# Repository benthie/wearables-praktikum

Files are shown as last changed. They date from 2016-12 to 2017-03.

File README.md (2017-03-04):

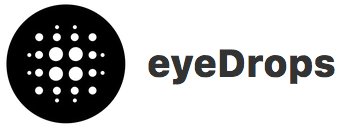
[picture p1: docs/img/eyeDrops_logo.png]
<br>
<i>     a project by Marlene Fiedler, Lorenz Miething and Benjamin Thiemann</i><br>
<br>
In the context of the lab course "Wearable Computing Systems", which started at the end of Oct 2016, we were asked to build our own wearable device. Our idea since then was to build a blink detection system that recognizes the user's lack of blinking when sitting in front of the computer. With a distance sensor that is monitoring the eye and a custom-built software the user of our wearable will be stimulated to blink by blurring the computer screen.

#Documentation

Now - at the end of the project - we proudly present our results. All the single bits and pieces of our project have been documented in order to deliver high reusability for anybody who wants to work on the project after the end of the semester the lab took place. This repository is mainly devided into the two sub parts hardware and software. The hardware itself consists of two different PCBs and the fixation parts to fix the PCBs to different kinds of glasses, as well as 3D printed glasses for users who usually do not wear any. All documenting files should enable you to rebuild the hardware such that you have a working system, which will be accepted by the software parts and then run without difficulty.<br>
<br>
The developed software has been published under the open source MIT License and is running as it is. It consists of two parts, namely an RFduino sketch and a Mac OS X Cocoa application. The sketch for the RFduino contains the blink detection algorithm and is able to communicate with the Cocoa app via Bluetooth Low Energy. For detailed information about the blink detection algorithm please see [here](#eye-blink-detection-algorithm). The Cocoa app's source code has both copious commenting and a [Doxygen documentation](https://benthie.github.io/wearables-praktikum/). The application's graphical user interface will be explained [below](#eyedrops-cocoa-application) and is additionally explained in a short [video](https://youtu.be/3qRnkdi4qJQ).

##Table of contents
- [Requirements](#requirements)
- [How to use](#how-to-use)
- [Hardware](#hardware)
  - [VCNL4020](#vcnl4020)
  - [RFduino](#rfduino)
  - [3D-printed parts](#3d-printed-parts)
- [Eye blink detection algorithm](#eye-blink-detection-algorithm)
- [eyeDrops Cocoa Application](#eyedrops-cocoa-application)
  - [Blur mode](#blur-mode)
  - [Bluetooth connection](#establishing-bluetooth-le-connection)
  - [User profile manager](#user-profile-manager)
  - [Preferences](#preferences)
  - [Calibration](#calibration)
  - [Ready to use](#ready-to-use)
  - [Executable File](#executable-file)
  - [Doxygen documentation](https://benthie.github.io/wearables-praktikum/)
- [Live Demo](#live-demo)
- [Credits](#credits)
- [License](#license)

###Requirements
- Arduino IDE ([Arduino software](https://www.arduino.cc/en/main/software)) 
- RFduino Package ([Link to the Git](https://github.com/RFduino/RFduino/blob/master/README.md))
- Mac OS X (sorry for that crucial restriction!)
- Bluetooth Low Energy (BLE - also called Bluetooth 4.0) capable Mac
- RFduino USB Shield ([RFD22121](http://www.rfduino.com/product/rfd22121-usb-shield-for-rfduino/index.html) or [RFD22124](http://www.rfduino.com/product/rfd22124-pcb-usb-shield-for-rfduino/index.html))
- CorePlot Framework ([Installation Guide](https://github.com/core-plot/core-plot/wiki/Using-Core-Plot-in-an-Application))

###How to use

So how to use our wearable? Simply grab the 3d-printed clips and the fitting slider, mount the electronics together with a battery pack on it, which then altogether forms the so called "<b>wearable</b>" and make sure that your Mac fullfills the above requirements. Plug the RFduino USB shield into your Mac and upload our [RFduino sketch](software/RFduino) to the wearable. After completing this step the last thing to do is to download the [Xcode project](software/cocoa-app), follow the [CorePlot library installation guide](https://github.com/core-plot/core-plot/wiki/Using-Core-Plot-in-an-Application) and start the eyeDrops application and have fun exploring.<br>
<br>
<i>Note:</i> If you want to use the compiled and built application (.app file) please follow the steps described in section [Executable File](#executable-file).

#Hardware

Our Hardware consits mainly of three parts: The sensor that is detecting the blinks, the microcontroller RFduino and our 3D-printed parts, used to hold the sensor and microcontroller in place.

##VCNL4020

The sensor used in our wearable is the VCNL4020 (http://www.vishay.com/docs/83476/vcnl4020.pdf). It is a proximity and ambient light sensor with a built-in infrared emitter and photo diode. The data obtained from the sensor vary, depending on how much light is reflected back to the sensor. Due to its high 16-bit-resolution and the operating range from 1 to 200 mm, it is possible to determine the difference of distance when pointing at an open or a closed eyelid. The data of the VCNL4020 can be transferred via an I²C Interface. Furthermore, interrupts can be sent. 

<p align="center">
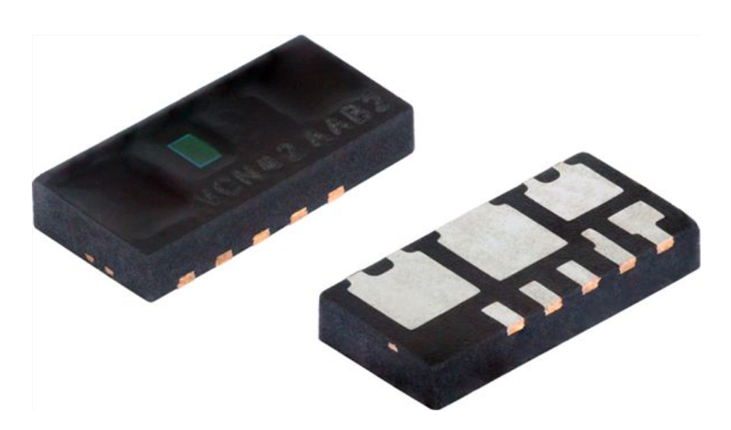
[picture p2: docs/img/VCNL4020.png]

<br>Figure 1: Sensor VCNL4020.
</p>

A custom PCB was designed for the VCNL4020. The goal was to get a board that can be attached to a clip, mounted in the front of spectacles, worn by the user. In order to not disturb the user while working, the PCB should be as small as possible. The first design featured pull-up resistors for the data, clock and interrupt signals, decoupling capacitors and five header pins for power supply, the I²C interface and the interrupt signal. 

<p align="center">
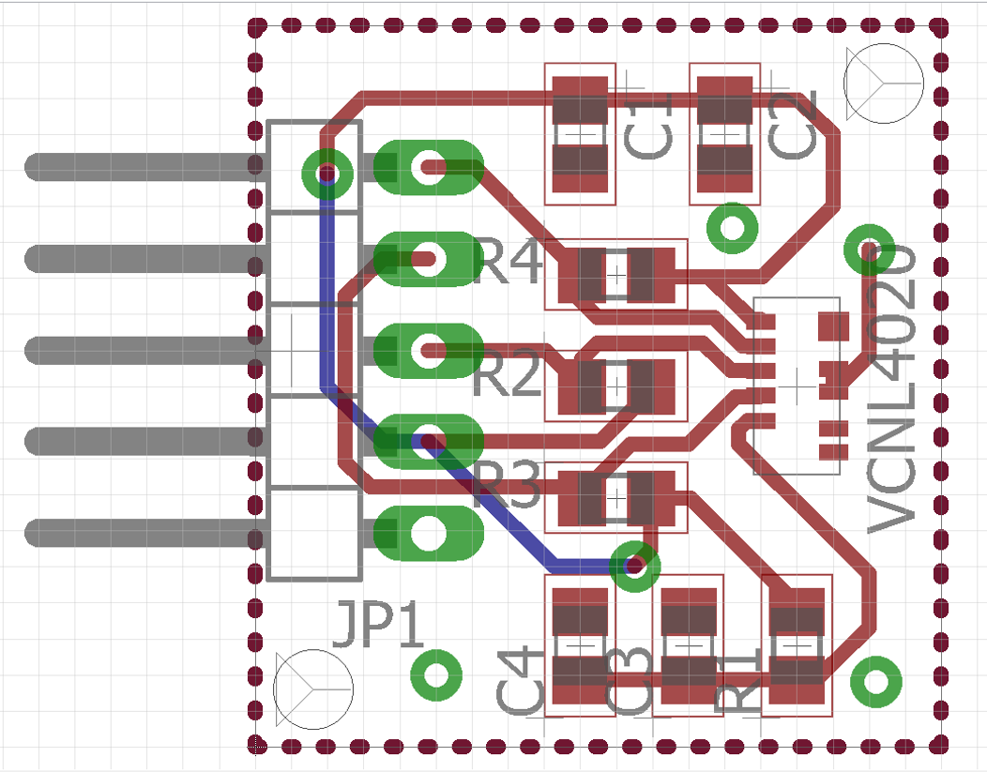
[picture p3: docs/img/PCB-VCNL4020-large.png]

<br>Figure 2: First PCB design for VCNL4020.
</p>

However, the first PCB design had to be revised due to its size, by moving the pull-up resistors to the second PCB and using small pads instead of the header pins. The revised PCB features a size of only 11 mm times 12 mm. The schematics and layouts of both versions  can be found [here](https://github.com/benthie/wearables-praktikum/tree/master/hardware/eagle).

The revised PCB was milled, using a Cirqoid CNC mill (http://cirqoid.com/). Both the milled PCB without components and the populated PCB can be seen here:

<p align="center">
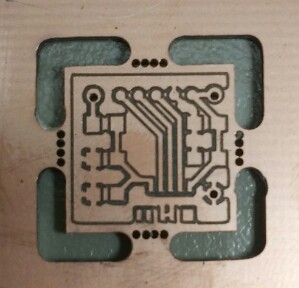
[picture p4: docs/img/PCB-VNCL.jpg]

<br>Figure 3: milled PCB for VCNL4020.
</p>

<p align="center">
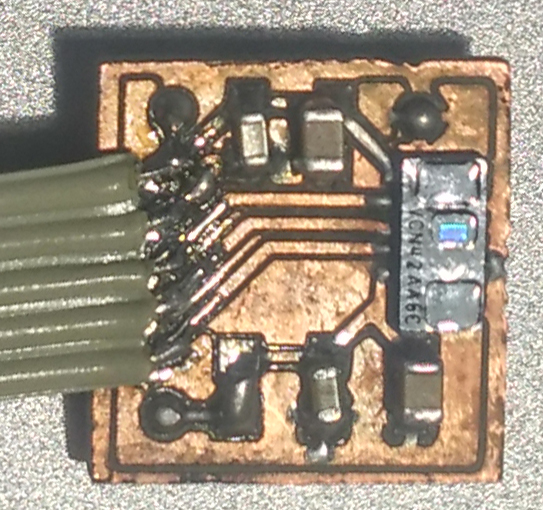
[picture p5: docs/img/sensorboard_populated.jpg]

<br>Figure 4: populated PCB for VCNL4020.
</p>

A ribbon cable was attached to the pads, so that the PCB for the VCNL can be connected to the RFduino PCB, which will be described in the following chapter.

##RFduino

The microcontroller used in our project is an RFduino (http://www.rfduino.com/) which features a bluetooth low energy (BLE) compatible radio transceiver. It can be programmed using the Arduino IDE.

<p align="center">
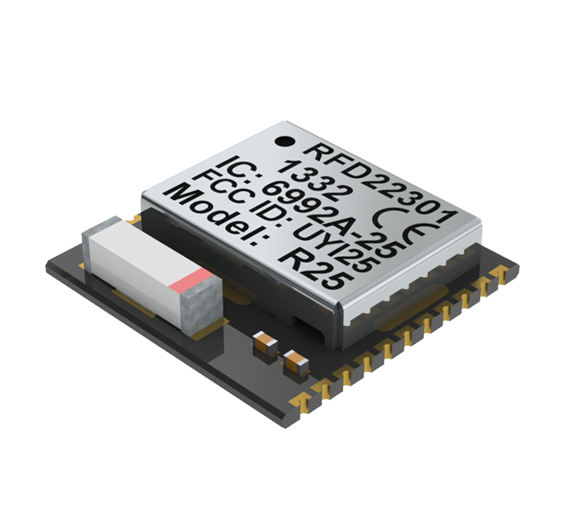
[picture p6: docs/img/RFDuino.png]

<br>Figure 5: RFduino
</p>

A custom PCB was made for the RFduino, featuring a 3.3 V voltage regulator, decoupling capacitors, a reset button, the mentioned pull-up resistors for the VCNL4020, header pins to connect to the ribbon cable leading to the VCNL4020 PCB, header pins for programming the RFduino and a screw terminal for the input voltage. The populated PCB can be seen here:

<p align="center">
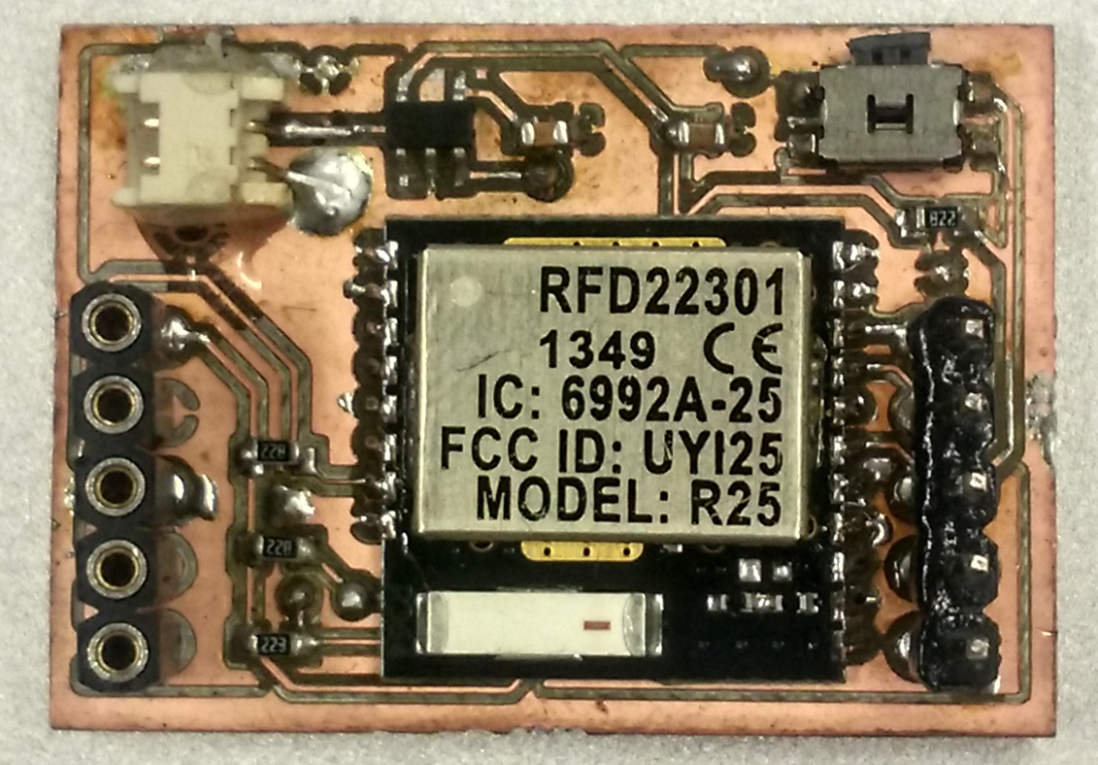
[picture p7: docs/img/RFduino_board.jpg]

<br>Figure 6: PCB for RFduino 
</p>

The schematic and layout of the PCB can be found [here](https://github.com/benthie/wearables-praktikum/tree/master/hardware/eagle).

#Eye blink detection algorithm

The blink detection algorithm can be divided in a filtering and a processing stage. The logarithmically scaled incoming raw data of the sensor are converted into distances of arbitrary unit. Any offset is removed by computing the differences between the samples and an equally weighted moving average filter with a window size of 16 (experimentally determined) is applied to the derivative of the data. With that, the filtering stage is completed and the actual detection algorithm begins, which is applied to the last 200 samples.<br>
Instead of going through all samples within that window for every new sample, the characteristic values are kept in real time as the samples come in.<br>
In order to understand the algorithm more easily let’s first have a look at the pattern that has to be detected. Since the different eye blinks vary in duration and peak height as shown in figure 7, the algorithm has to accomodate for this dynamic behaviour. 
<p align="center">
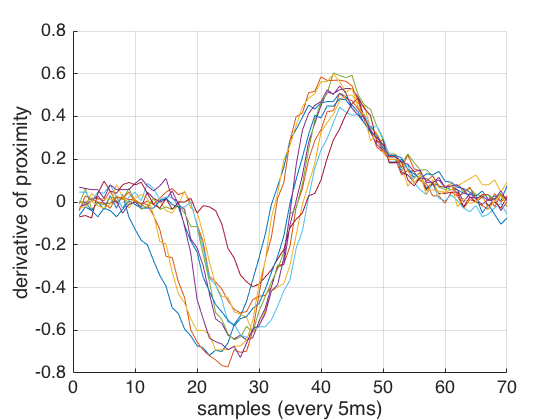
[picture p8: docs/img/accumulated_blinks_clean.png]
Accumulated eye blinks

<br>Figure 7: Accumulated eye blinks with varying durations from single person
</p>
Therefore, a simple pattern correlation would not perform very well. Instead, the algorithm looks for a certain dynamic pattern in the preprocessed data. It performs edge detection and zero crossing detection by comparing the current value with the previous one. The values are split into four areas: above positive threshold, between positive threshold and zero, between zero and negative threshold and below negative threshold. With this in mind six different crossings can be detected creating the following algorithm to detect the actual eye blink as shown in figure 8.
<p align="center">
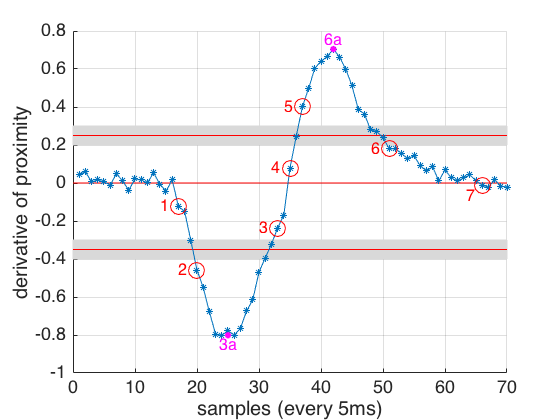
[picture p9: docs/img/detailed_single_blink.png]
Step by step eye blink

<br>Figure 8: Step by step blink detection
</p>
1. Zero has to be crossed from a positive to a negative value. This means that the measured distance is decreasing and the eye lid is closing. Zero was just cross for point 1.
2. The negative threshold is crossed downwards. This means that the measured distance decreases less significantly and the eye lid stops closing.
3. The negative threshold is crossed upwards. At this point the minimum value and its index between the two negative threshold crossings is determined from the sample buffer. If the sample number between the initial zero crossing and the determined minimum value is within a certain range and the minimim value is above a certain value. With that the first neces- sary condition is met and the blink level indicating the progress of the current eye blink to be detected is increased by one.
4. Zero is crossed upwards. This does not affect the algorithm and can happen multiple times with alter- nating downward zero crossings at this stage. The number of zero crossings is recorded for further anal- ysis at a later stage of the algorithm and refers to the duration the eye is closed during an eye blink.
5. The positive threshold is crossed upwards. This means that the eye lid is beginning to open again.
6. The positive threshold is crossed downwards. At this point the maximum value and its index between the two positive threshold crossings is determined. If the sample number between the last minimum value and the maximum value is within a certain range, the number of zero crossings does not exceed a certain limit, the maximum value itself does not exceed a certain value either, and the blink level has a value of 1 indicating a previes eye closing event, the blink level is increased again by one. This means the eye is stopping to open and therefore almost open again. It is now assumed, that an actual eye blink was detected for real time application.<br>If any of the above conditions is not met, the blink level is reset to zero.
7. Zero is crossed downwards. If the overall duration of the eye blink is within a certain range the blink detection is complete, the blink level is reset to zero and an eye blink is reported. This means that the eye is fully open again or at least the eye lid movement cannot be detected by the sensor anymore for the remaining eye opening procedure.

The actual threshold crossing detection is extended with a hysteresis procedure. In order to cross a threshold upwards the threshold plus a hysteresis value has to be crossed.
In order to cross it downwards, the threshold minus a hysteresis value has to be crossed. This ensures, that a small fluctuation in the data caused by noise does not mess up the steps of the algorithm. The hysteresis is shown as a gray area in figure 8.<br>
Testing this algorithm on multiple persons showed that it does not necessarily work out of the box for everybody but certain paramaters such as the thresholds, hysteresis and sample distances between the steps have to be adjusted. As shown in figure 7 the durations and peak values for only a single person differs from eye blink to eye blink. Looking at the data for different persons this varies even more.

##3D-printed parts

The 3D-printed parts include a clip and slider for the VCNL4020 PCB, a clip for the RFduino and spectacles for users who do not usually wear them. These parts were designed using the 3D CAD software Solidworks (http://www.solidworks.de/) and printed using the 3D-printer Makerbot Replicator 2X (https://store.makerbot.com/printers/replicator2x/). The used filament consists of ABS.

<p align="center">

<br>Figure 9: 3D-Printer Makerbot Replicator 2X
</p>

Since our product shall be usable with the users own spectacles, both clips were designed in three different sizes, so that they can be attached to temple arms of different widths. The clip for the VCNL4020 was made as small as possible and printed with transparent filament, in order to reduce the impact in the visual field of the user.

<p align="center">
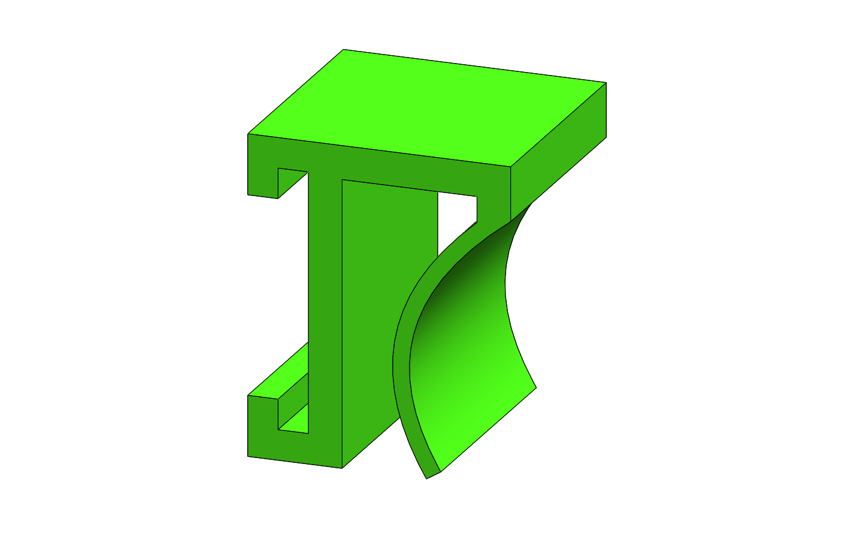
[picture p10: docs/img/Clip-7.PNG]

<br>Figure 10: Clip for VCNL4020 PCB
</p>

Due to different anatomies of different users, like smaller or bigger eyes, eyeballs located further in- or outside the head, etc., it should be possible to adjust the position of the VCNL4020 PCB. Therefore, the PCB is not directly attached to the clip, but instead attached to a slider, which is itself slided into the clip.

<p align="center">
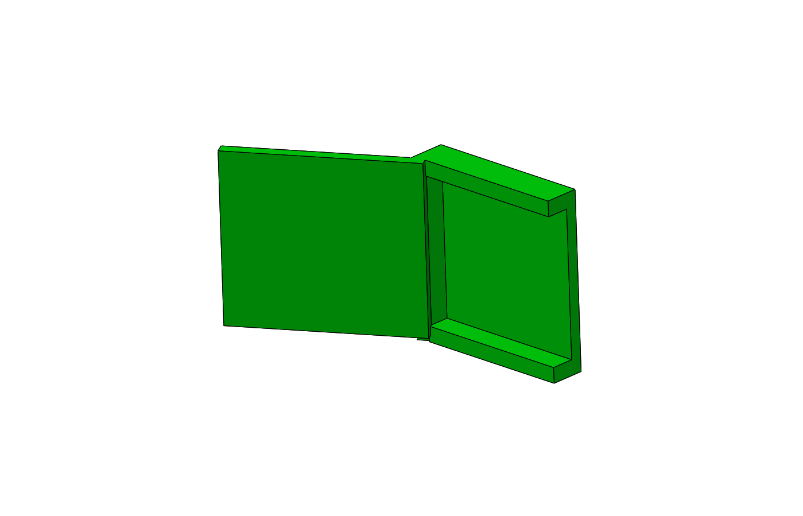
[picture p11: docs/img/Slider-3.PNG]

<br>Figure 11: Slider for VCNL4020 PCB
</p>

The slider was designed with different inclinations, so that the angle between the temple arms and the PCB can be adjusted. There are also sliders that lower the position of the PCB with respect to the height of the temple arms. These exchangable sliders allow adjustment to different anatomies.

<p align="center">
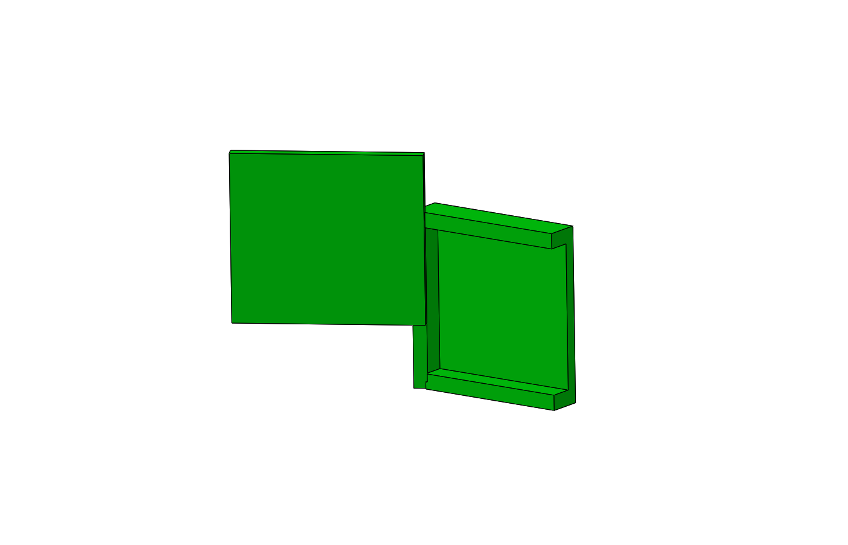
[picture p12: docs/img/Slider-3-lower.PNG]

<br>Figure 12: lower Slider for VCNL4020 PCB
</p>

In order to make adjustments easier, we designed further clips containing magnets. With these, it was possible to attach magnet-containing 3D-printed adapter that were stuck to the PCB. These adapters were also printed with different inclinations, so that, depending on the users anatomy, the sensor would always be well adjusted. However, very thin magnets were not strong enough to hold the adapter in place and thicker magnets were too thick, so that the PCB was encountered disturbing for the user.
Another approach was a 3D-printed ball joint, which could not be used neither, due to the low printing quality for very small round objects. <br>
<br>

In order to attach the RFduino PCB to the users spectacles, there is another clip. This clip is used without a slider. Instead the PCB is directly attached to the clip, held by two tappets. There is a cavity in the clip, so that the reset button of the PCB can be pressed easily.

<p align="center">
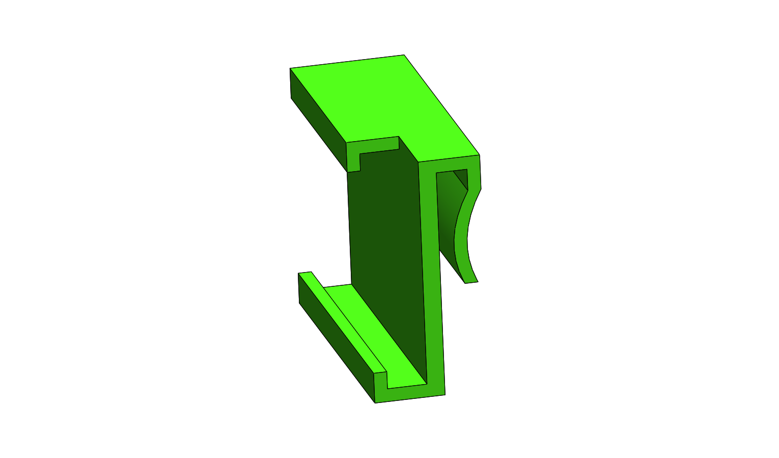
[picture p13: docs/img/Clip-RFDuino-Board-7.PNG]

<br>Figure 13: Clip for RFduino PCB
</p>

The 3D-printed spectacles with the attached clips can be seen in the following graphic:

<p align="center">
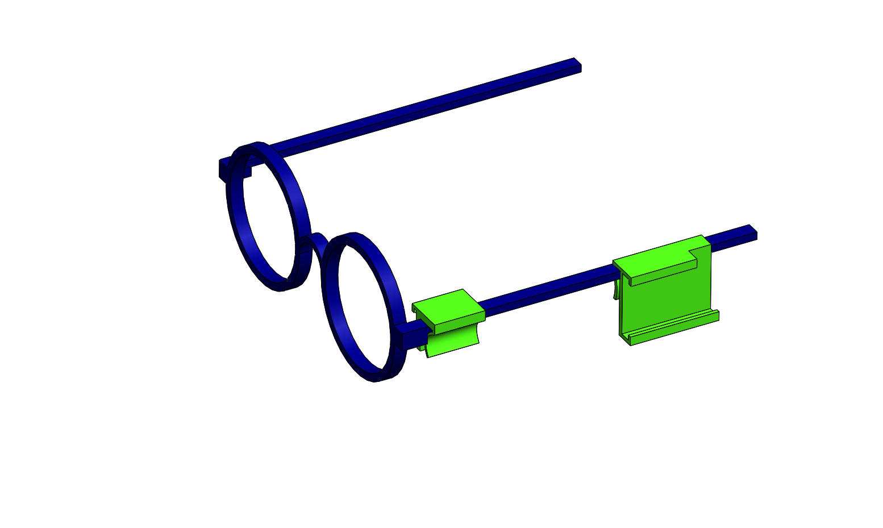
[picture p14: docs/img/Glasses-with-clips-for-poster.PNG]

<br>Figure 14: Spectacles with clips 
</p>

The SLDPRT-files as well as the 3D-printing-files for the described parts can be found [here](https://github.com/benthie/wearables-praktikum/tree/master/hardware/3dprinting).

#eyeDrops Cocoa application

The eyeDrops application is designed to offer a highly comfortable interface between the user and the wearable. The main task of the entire system is to detect a lack of blinking and then react correspondingly. Our implemented reaction to such a lack of blinking is a progressive blurring of the screen in order to enforce an eye blink. A blurred screen can be cleared by a simple blink, which was apparently long overdue. And since the app only needs to control the screen, it was designed as a pure menubar application, that is having no active window but just an icon in the menu bar.<br>
<br>
We chose Mac OS X as the target operating system after a long period of attemps (with a lot of effort) to deliver a platform independent software for our wearable. In the end it was a sum of facts that influenced our decision. The main problem, to begin with, was to build a software that is able to blur the complete screen. Here, Java was the first programming language we tried, but we could not achieve a working version. To do so, one would have to enter a very low level graphics programming since Java cannot make use of a window compositing manager. With Cocoa and Objective-C on the other hand, we could deliver a working blurring of the screen by simply using Quartz Compositor of OS X. In the following process we tried to stick to Java for the main program, but then there was no working BLE stack for Java around that would work on all desired platforms (Windows, Mac, Linux) and thus there was no need to stick to Java anymore. Since two third of the developers were using a Mac and we already had a working software for blurring the screen, it stood to reason that we write the complete software just for Mac. And that is what we did after all.<br>
<br>
To get the eyeDrops application running, download the source code from the [software folder](/software/cocoa-app) and launch `eyeDrops.xcodeproj` with Xcode. Make sure that you properly include the CorePlot framework as described [here](https://github.com/core-plot/core-plot/wiki/Using-Core-Plot-in-an-Application). The project is now ready to be built. The following documentation explains how to use the application you should be able to see now.

##Blur mode

<p align="center">
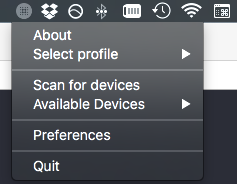
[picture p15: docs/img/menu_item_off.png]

<br>Figure 15: Application in off state.
</p>

As you can see in figure 15, there is no active window but only a menubar icon which pops down a usual menu when you click on it. In the above image the icon is gray and not white, telling the user that blur mode is turned off.

<p align="center">
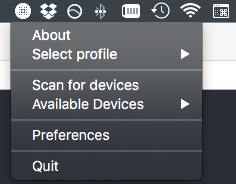
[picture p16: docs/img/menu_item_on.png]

<br>Figure 16: Application in on state.
</p>

In figure 16, however, the icon is white and thus signalizing that blur mode is activated. To switch bewteen those two states simply <b>ctrl-click</b> on the menubar item. If blur mode is actived and in case that a device is connected, the screen would be blurred if the user did not blink in adjustable time interval. See the [settings](#preferences) section for more information about the allowed time interval without an eye blink.

##Establishing Bluetooth (LE) Connection<a name="establishing-bluetooth-le-connection" />

In order to establish a bluetooth connection with the wearable, which is the next necessary and logical step when setting up the system, the first thing to do is scanning for bluetooth nearby. This can be either done via the menuitem <i>Scan for devices</i> or automatically by the app. The latter way needs a setting in the <i>General</i> tab in the [Preferences Window](#preferences).<br>
<br>
After a successful scan all the available devices are listed in the submenu <i>Available Devices</i>. Connecting to the device can again be done either via selecting the corresponding menuitem or automatically by the app. The second way needs a setting in the <i>General</i> tab in the [Preferences Window](#preferences).<br>

<p align="center">
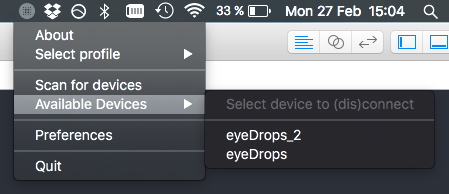
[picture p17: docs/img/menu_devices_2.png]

<br>Figure 17: List of available devices.
</p>

A connected device is represented with a check mark next to its name. Another click on that same menuitem would then cancel the connection with the device. Selecting another device which is currently not the connected one would simply switch the connection to that device.<br>
<br>
In case that a connection was successfully established, the wearable now needs a user profile to work with. This user profile contains the paramerters used by the blink detection algorithm. Without a valid user the wearable will be idle.

##User profiles / profile manager<a name="user-profile-manager" />

In order to obtain a valid user profile either load an XML file containing one or more valid profiles or use the systems [calibration](#calibration) procedure to create a new profile.

<p align="center">
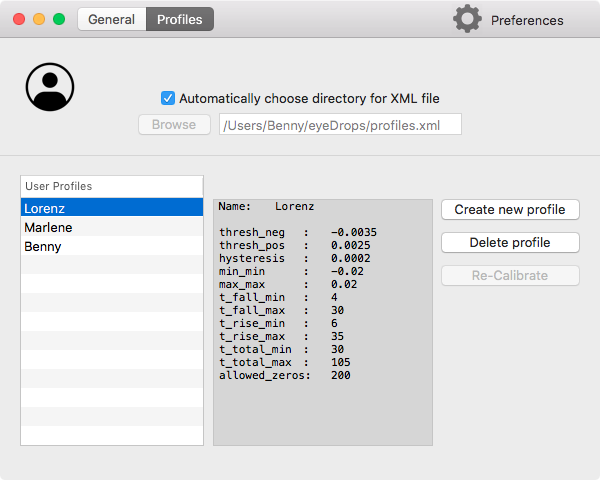
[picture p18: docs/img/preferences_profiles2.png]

<br>Figure 18: Preferences - User profile manager.
</p>

The default directory the app is working in is `/Users/<CurrentUser>/eyeDrops` = `~/eyeDrops`, where `<CurrentUser>` is the name of the currently logged in user. This directory is created during the app's launching process and will of course not be overwritten if it already exists. You can put your XML file in this directory and restart the app, which will lead to an automatic reading of the profiles contained in XML file, or you click <i>Browse</i> in the <i>Profiles</i> tab in the Preferences Window (see figure 18) and manually select your XML file there. After setting the new path, the profiles will be automatically read from the file and displayed in the TableView in the profile manager. Selecting a profile from that table will display the user profile's content in the TextView next to the table. It is also possible to delete a profile by clicking <i>Delete profile</i> or to create a new profile by clicking <i>Create new profile</i>, which will then open up the [calibration window](#calibration).

##Preferences

The system wide settings can be changed in the <i>General</i> tab in the Preferences Window (see figure 19). When starting the eyeDrops app for the first time, this settings will be initialized with values we used during the development phase. When properly closing the app, all made changes will be stored in `settings.txt` in the default directory and reloaded at the next launching process. That way your settings do not get lost.

<p align="center">
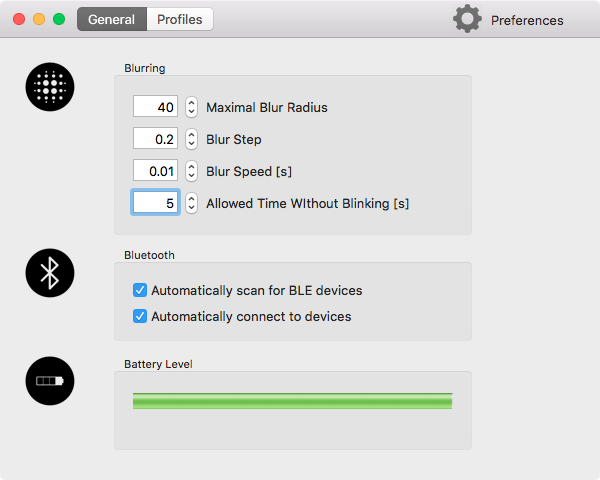
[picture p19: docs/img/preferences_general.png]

<br>Figure 19: Preferences - General settings.
</p>

###Blurring settings
- <b>Maximal Blur Radius:</b> determines how strong your screen gets finally blurred.
- <b>Blur Step:</b> determines the step increase while blurring (the smaller the value, the smoother the blurring).
- <b>Blur Speed:</b> determines the time delay between two steps (the smaller the value, the longer the blurring up to the maximal radius takes).
- <b>Allowed Time Without Blinking:</b> the time interval in which at least one blink has to occur.

###Bluetooth settings
- <b>Automatically scan:</b> determines whether the app automatically scans for devices.
- <b>Automatically connect:</b> determines whether the app automatically connects to the last known device.

###Battery Level
- This LevelIndicator shows the battery level of the wearable. The indication here is not really proportional to the battery voltage but to the voltage after the voltage regulator in the PCB. <!--For more information about this see the [report TODO](/docs/report.pdf).-->

##Calibration

As explained above, calibration is essential for having a properly working blink detection algorithm. Since every eye is unique, differing shapes, sizes and positions in the skull are what the sensor is facing. And due to those inequalities the measured distances to the eye vary from one user to the other. The implemented calibration procedure let's the user define his or her individual calibration parameters, which are then uploaded to the wearable as well as stored in a profile on the computer. More information about the calibration and the different parameters used to detect a blink is elaborately described [above](#eye-blink-detection-algorithm).

<p align="center">
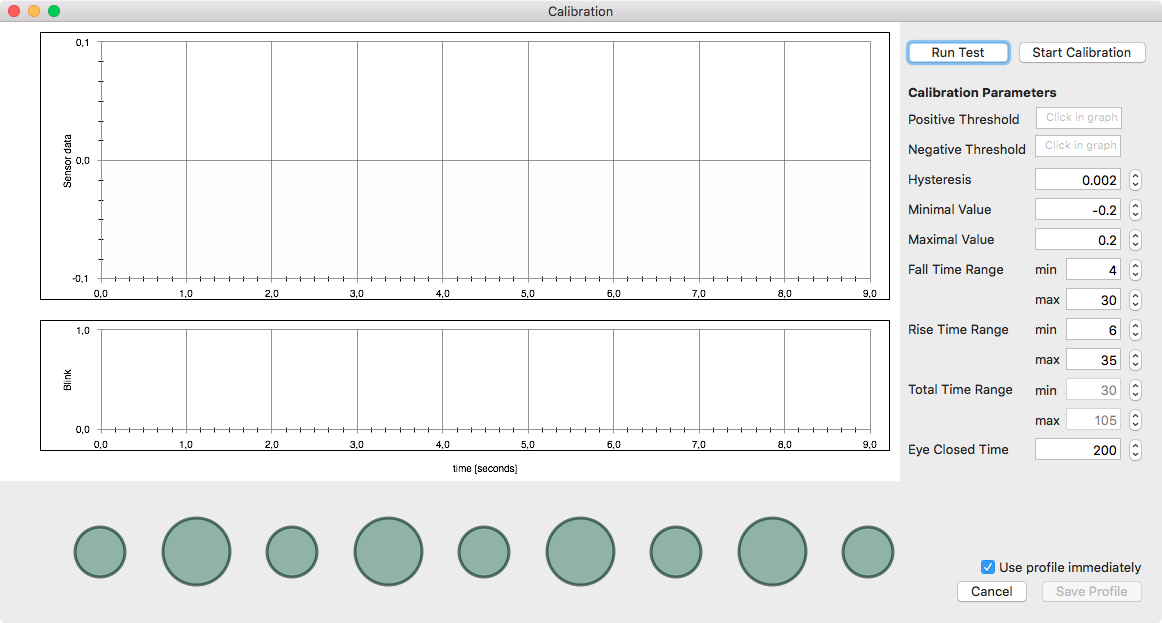
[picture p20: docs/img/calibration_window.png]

<br>Figure 20: Calibration window - On start-up.
</p>

Figure 20 shows the calibration window directly after start-up. Both eyeDrops app and wearable are now in calibration mode  where the RFduino can be triggered to continuously send data packages containing sensor raw data and information about whether a blink was detected or not until a stop message arrives.

<p align="center">

<br>Figure 21: Calibration animation (two successive steps).
</p>

A custom-built animation (see figure 21) is used to guide the user through the data acquisition phase of the calibration. This phase takes nine seconds and should contain four blinks (represented by the larger circles). It can be run testwise without receiving any data, just to get to know the procedure by clicking the button <i>Run Test</i>.<br>
<br>
The completion of the data acquisition will be announced by an pop-up alert with instructions for the next steps. Afterwards the data will be plotted in the two designated graphs.

<p align="center">
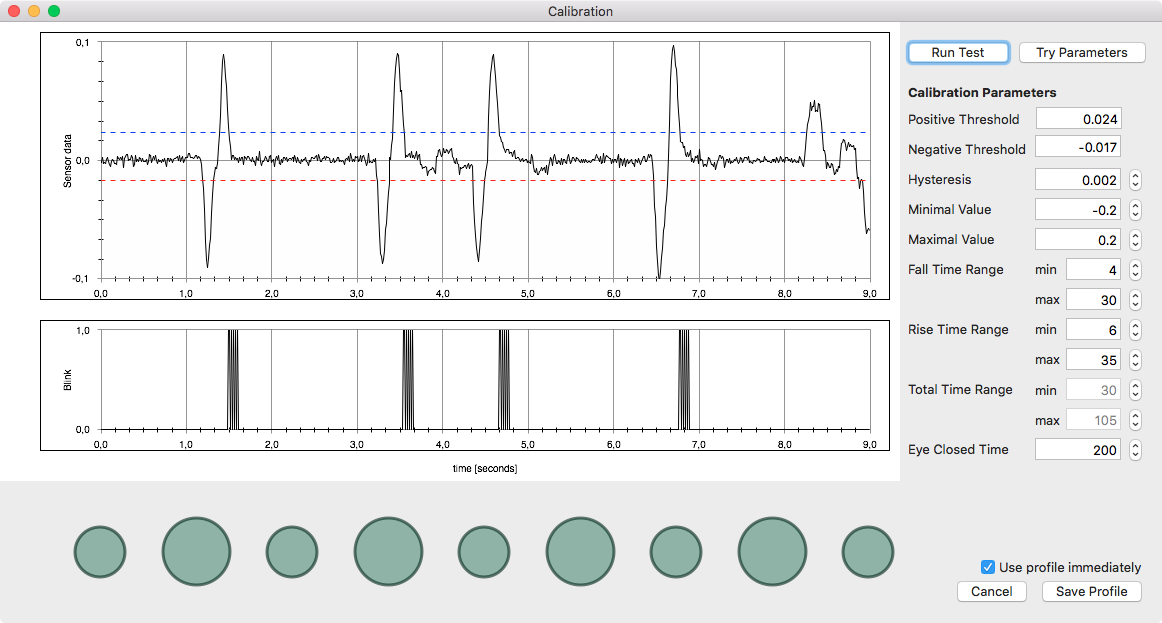
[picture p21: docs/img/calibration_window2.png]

<br>Figure 22: Calibration window - After receiving and plotting the sensor and blink data.
</p>

A completed data acquisition phase can be seen in figure 22. The preset values on the right side of the calibration window turned out to make sense for most of test users and can be adopted for new profiles without being worried about bad performance. The only two values that are mandatory to be set by the user are the threshold values. These can be obtained by simply clicking on the sensor data graph (top). A red and a blue line will appear for negative resprectively positive threshold. Place the lines such that any noise lies between the threshold values. A good guiding value is to set the thresholds to half of it's max value. After setting the threshold values the user can either do another calibration with the newly gained values and check if the algorithm now detects (more) blinks or directly save the profile with the option to directly use the new profile.<br>

###Ready to use

Now that a valid profile has been created and uploaded to the wearable, the system is ready to use. Enable the [blur mode](#blur-mode) and enjoy the experience with the system.

###Using the Cocoa executable (.app file)<a name="executable-file" />

If you do not want to always launch the application out of Xcode, you can use an executable .app file. After running the app out of Xcode, an .app file has been automatically created there. In your project navigator in Xcode you can find it in the `Products` folder. Right-click on `eyeDrops.app` and select `Show in Finder`. The opened folder contains the app as well as two frameworks. Those frameworks must be copied into `/System/Library/Frameworks` to make the `eyeDrops.app` launchable.

##Live Demo

[Link to youtube video](https://www.youtube.com/embed/3qRnkdi4qJQ)

##Credits

<b>The Noun Project - Source for the used items:</b>
- <i>Rohit M S:</i> Creator of the main icon
- <i>Nicolas Morand:</i> Creator of the profiles icon
- <i>Guilhem:</i> Creator of the battery icon
- <i>Viktor Vorobyev:</i> Creator of the bluetooth icon

##License

This project has been published under the MIT License.

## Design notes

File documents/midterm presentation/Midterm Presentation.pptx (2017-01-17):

## Wearable Computing Systems eyeDrops

Lab Course 2016 / 2017
Marlene Fiedler
Lorenz Miething
Benjamin Thiemann

Albert-Ludwigs-Universität Freiburg

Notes: Begrüßung

Name

Thema

## Contents

- Eye blink detection – proof of concept
- Components
- Clip design
- Printed circuit board
- Blurry screen
- Project plan

eyeDrops

## Eye blink detection – Sensors

- Ambient light sensor
  - APDS 9600 RGB ambient light and gesture sensor
    - First success but slow and not robust (active)

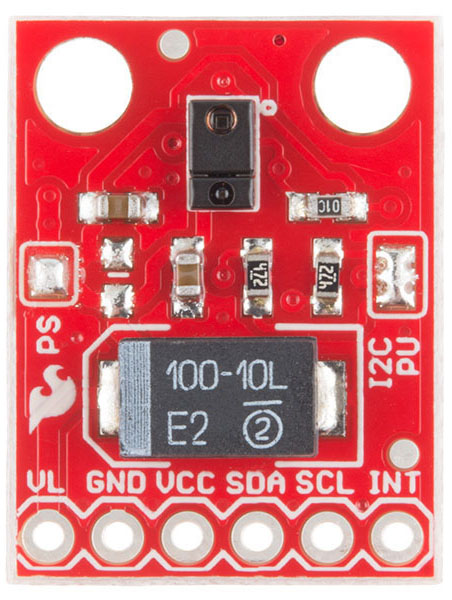
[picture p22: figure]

https://cdn.sparkfun.com//assets/parts/9/6/0/3/12787-02.jpg

## Eye blink detection – Sensors

- Ambient light sensor
  - APDS 9600 RGB ambient light and gesture sensor
  - Self built alternative using photodiode and analogue signal
    - Very fast but not robust (passive)

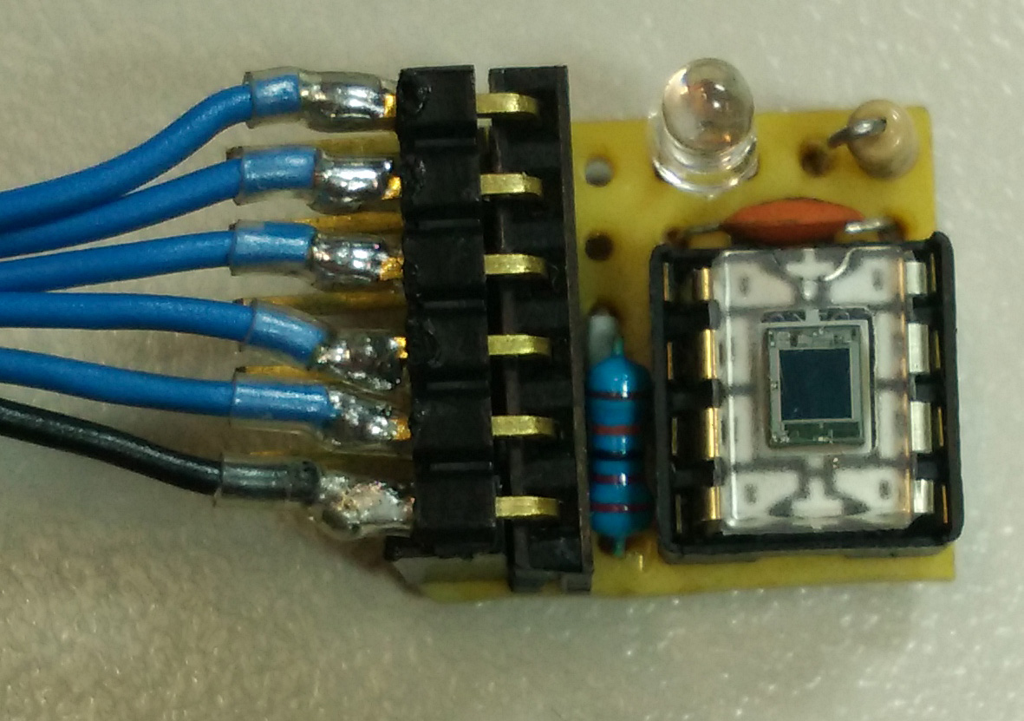
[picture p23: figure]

## Eye blink detection – Sensors

- Ambient light sensor
  - APDS 9600 RGB ambient light and gesture sensor
  - Self built alternative using photodiode and analogue signal
- Proximity sensor
  - VCNL 4010 ambient light and proximity sensor (active)
    - Fast enough and robust

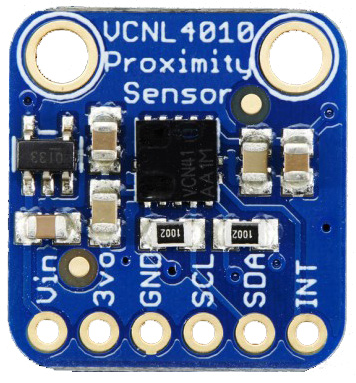
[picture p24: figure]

https://cdn-shop.adafruit.com/1200x900/466-05.jpg

## Eye blink detection – Software

- Capture record and visualize data using Processing

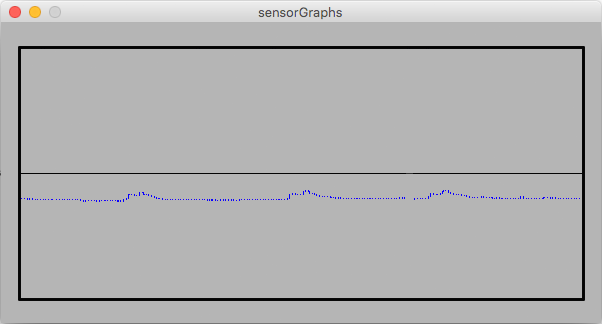
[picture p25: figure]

## Eye blink detection – Software

- Capture and visualize data using Processing
- Analyse and develop algorithm using MATLAB

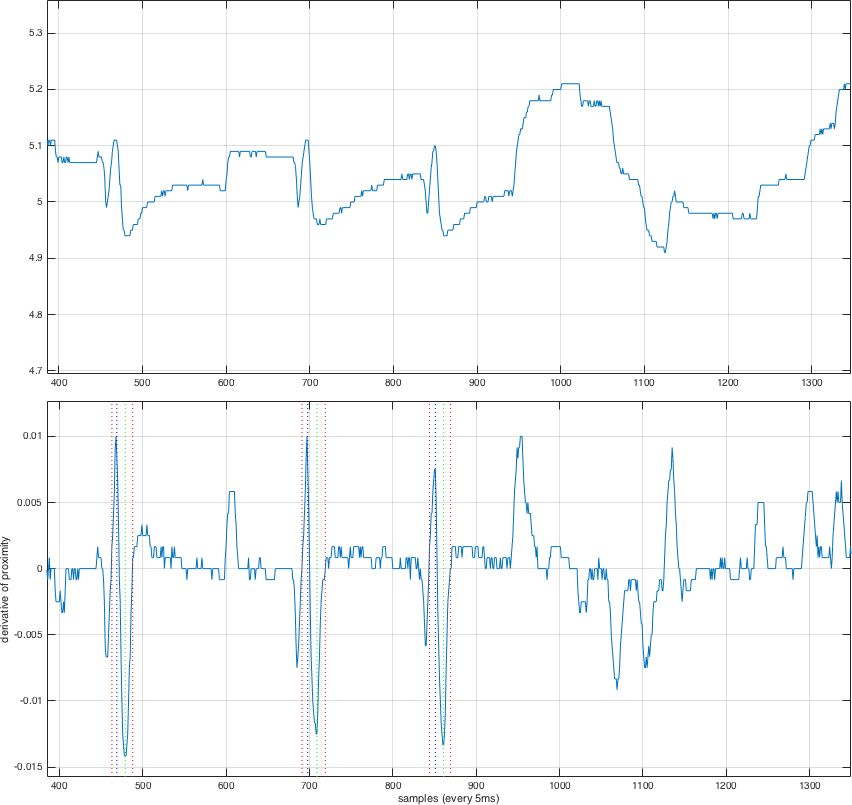
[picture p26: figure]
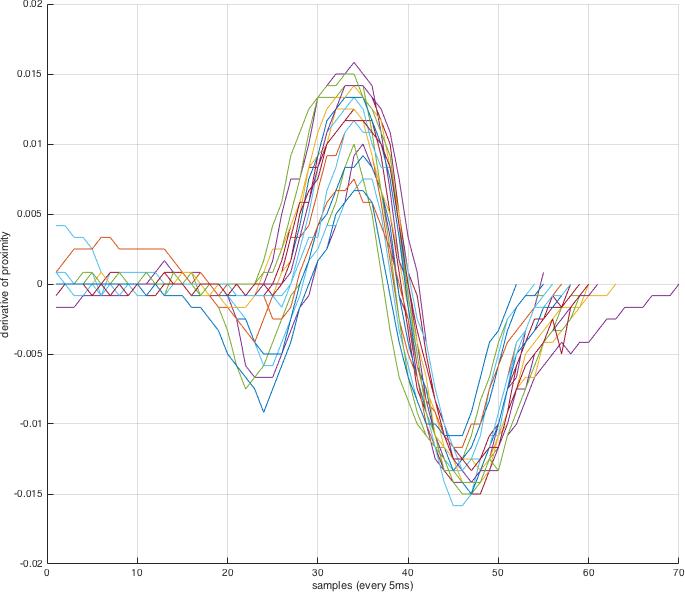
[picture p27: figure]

## Components

- RFDuino
  - Arduino compatible microcontroller
  - Bluetooth low energy RF module


http://www.rfduino.com/wp-content/uploads/2014/03/RFD22301.Prospective.Top_.png

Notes: Arduino compatible Microcontroller
With a bluetooth low energy RF module
We use SMD version
ADC
Interfaces: I²C, UART, SPI, GPIO
Wireless communication with iOS and android smartphones

## Components

- RFDuino
  - Arduino compatible microcontroller
  - Bluetooth low energy RF module
- VCNL4020
  - Ambient light sensor
  - Proximity sensor
  - Interrupt function

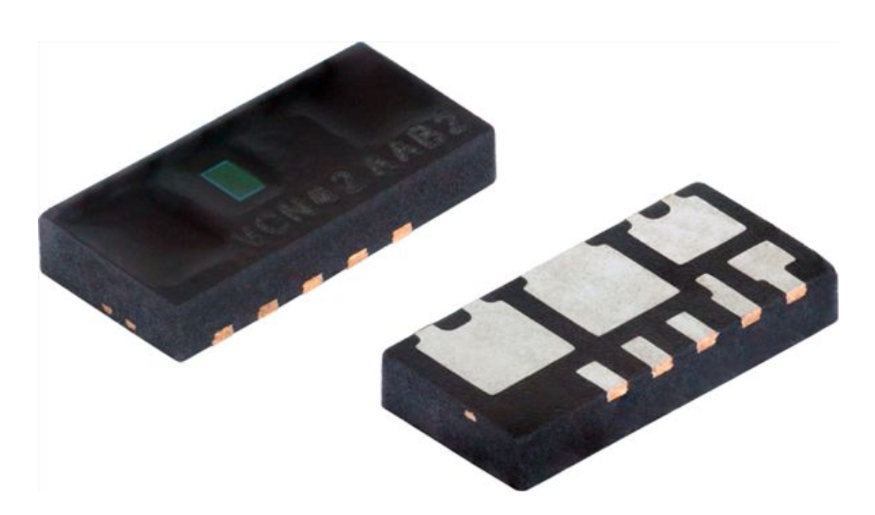
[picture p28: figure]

http://www.vishay.com/docs/83476/vcnl4020.pdf

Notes: I²C
Ambient light not used right now, maybe later

## Components

- RFDuino
  - Arduino compatible microcontroller
  - Bluetooth low energy RF module
- VCNL4020
  - Ambient light sensor
  - Proximity sensor
  - Interrupt function
- BNO055
  - Absolute orientation sensor

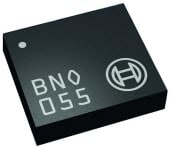
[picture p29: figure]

http://www.mouser.com/images/microsites/Bosch_BNO055.jpg

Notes: optional
Gyroscope, accelerometer, geomagnetic sensor
I²C, UART

## Assembly on glasses

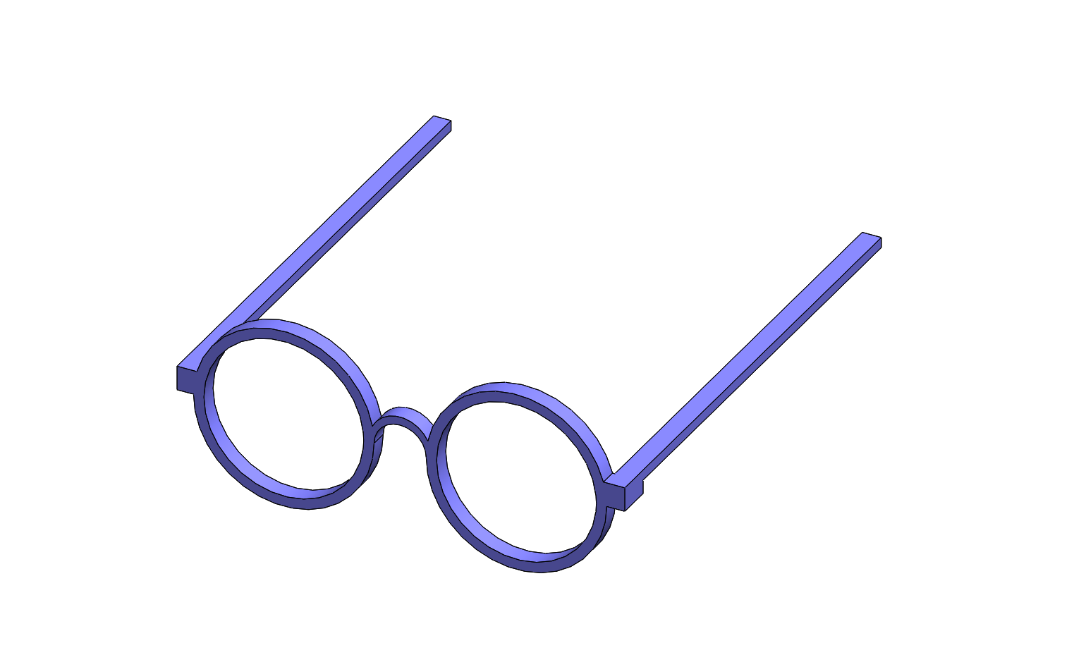
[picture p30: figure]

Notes: Gyroscope, accelerometer, geomagnetic sensor
I²C, UART

## Assembly on glasses

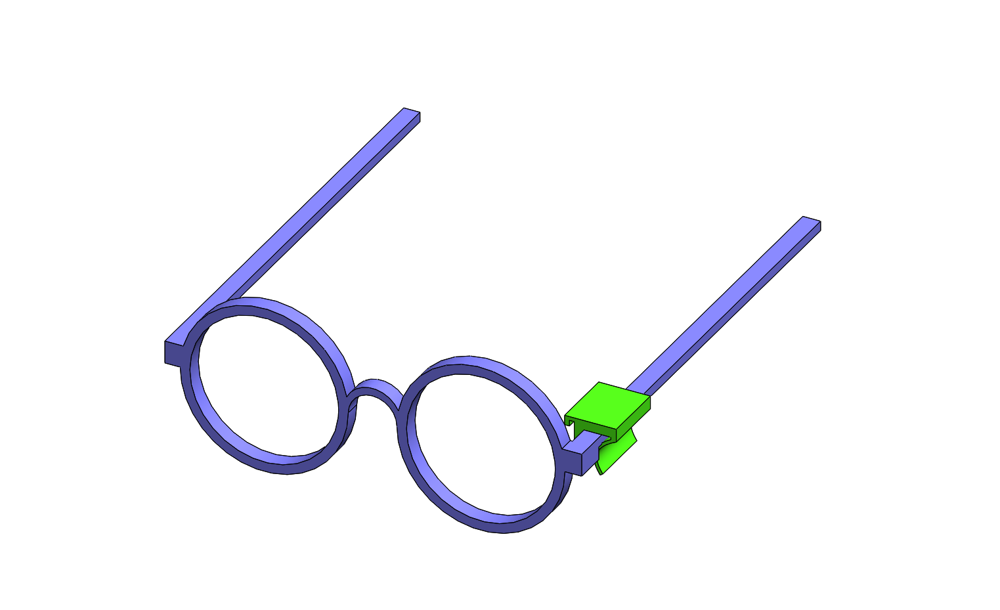
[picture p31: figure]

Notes: Gyroscope, accelerometer, geomagnetic sensor
I²C, UART

## Assembly on glasses

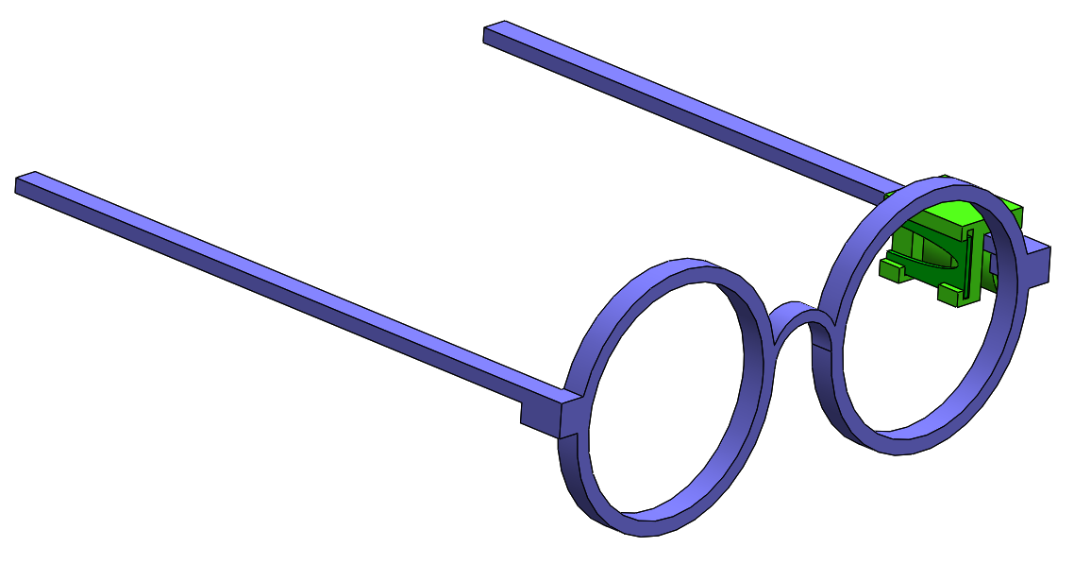
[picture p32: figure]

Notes: Gyroscope, accelerometer, geomagnetic sensor
I²C, UART

## Clip

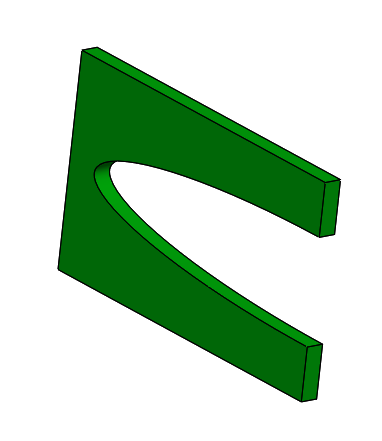
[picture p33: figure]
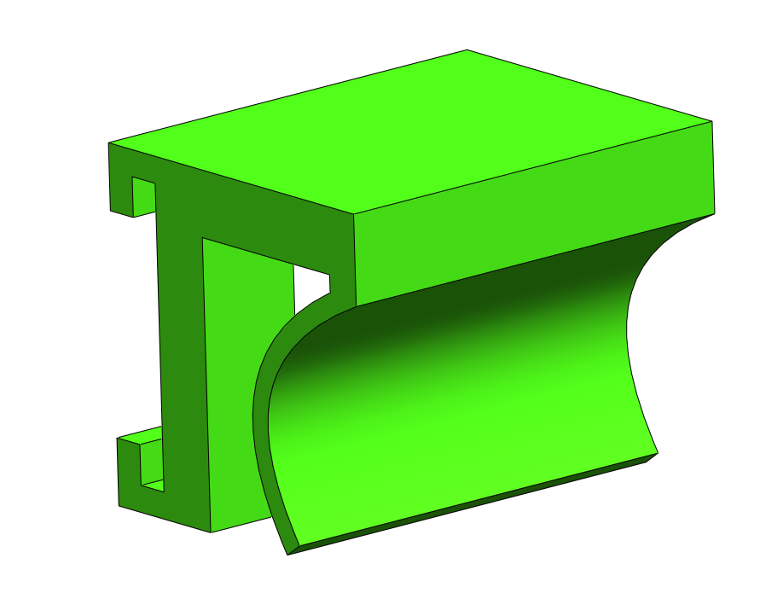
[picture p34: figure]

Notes: Gyroscope, accelerometer, geomagnetic sensor
I²C, UART

## Clip

www.anz-verlag.de

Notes: Gyroscope, accelerometer, geomagnetic sensor
I²C, UART

## PCB for VCNL4020

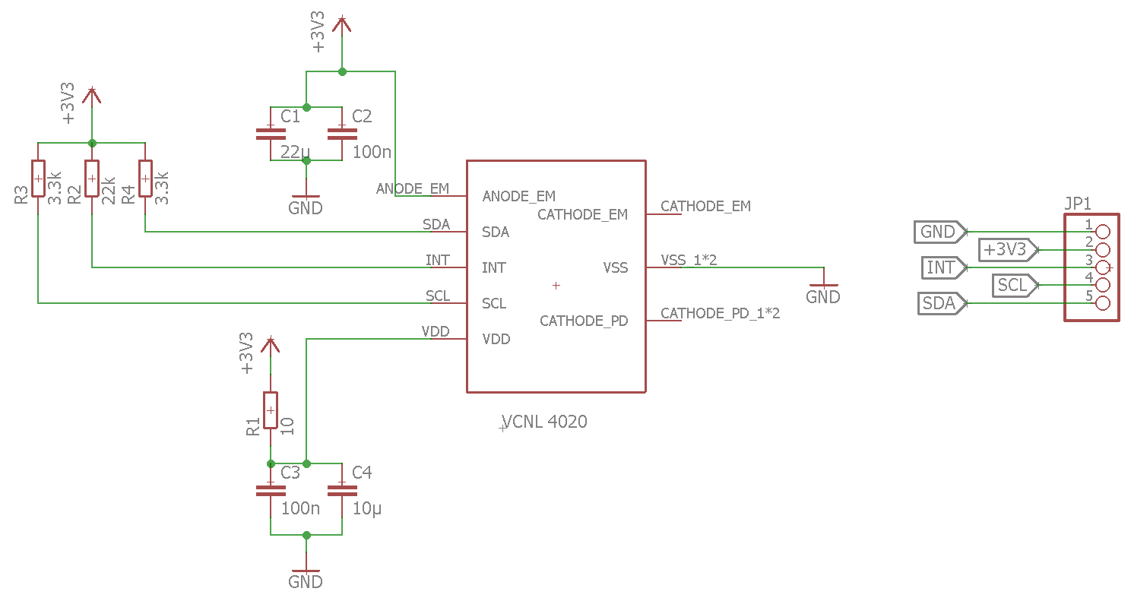
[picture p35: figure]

## PCB for VCNL4020

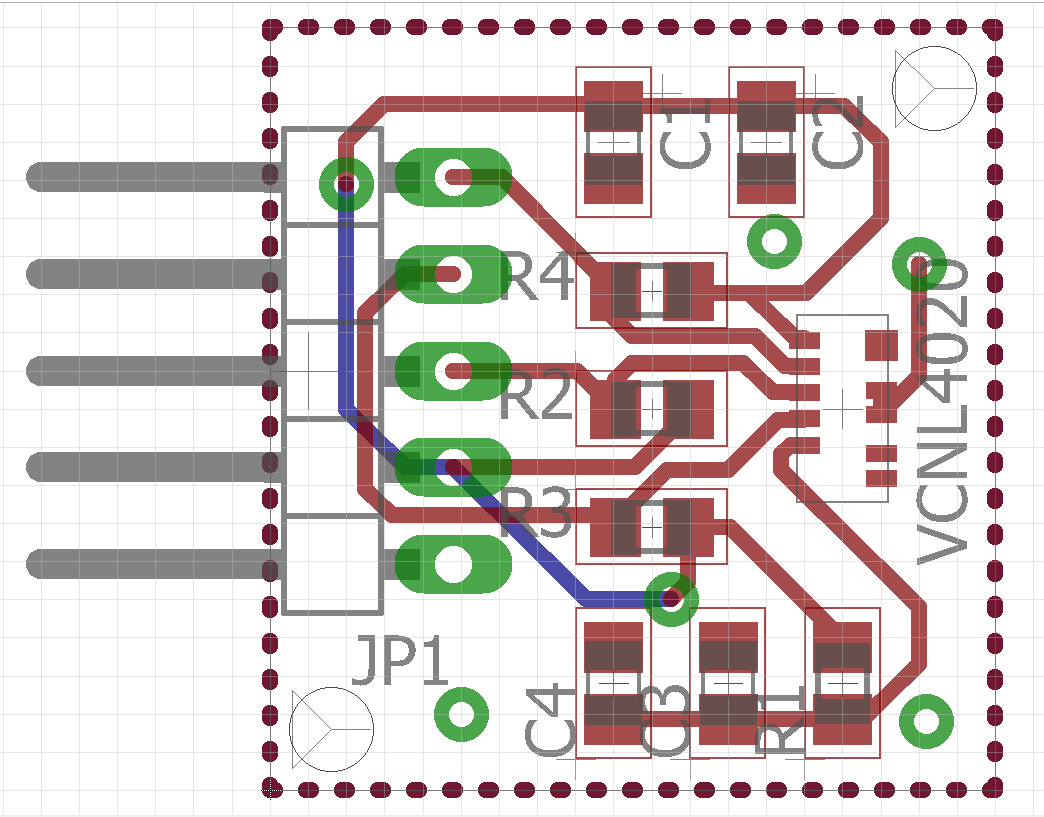
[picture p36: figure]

## PCB for VCNL4020 – smaller

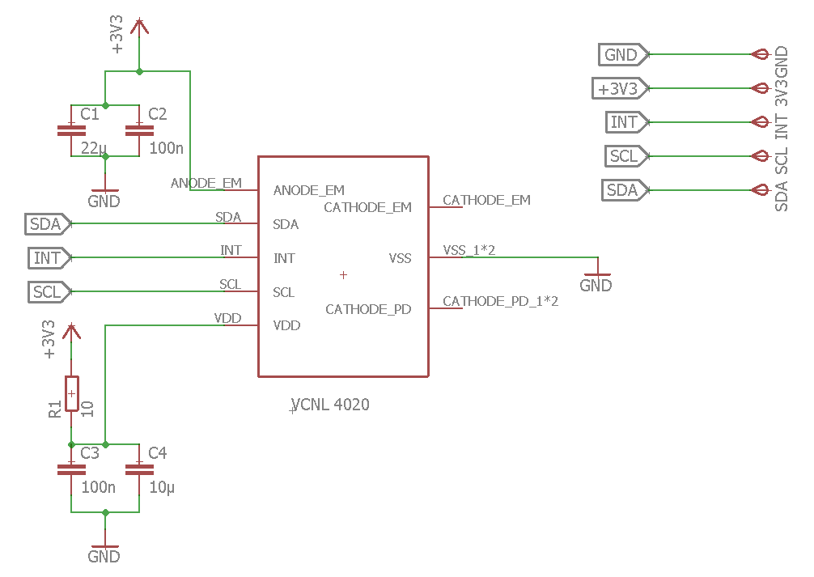
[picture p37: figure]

## PCB for VCNL4020 – smaller

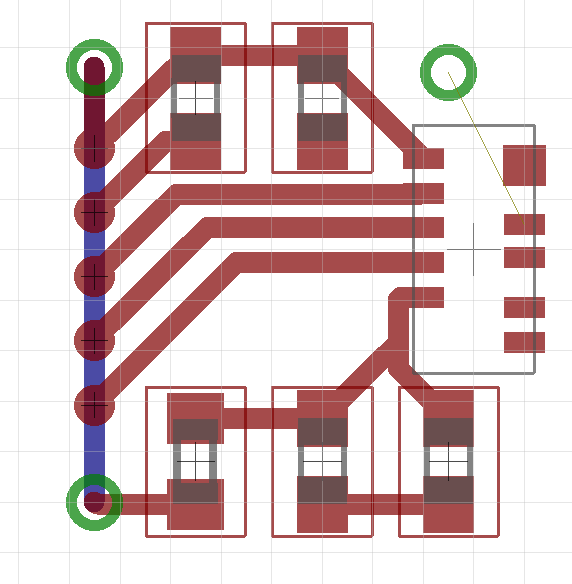
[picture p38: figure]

## PCB for VCNL4020

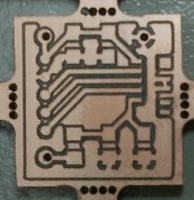
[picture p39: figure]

## PCB for RFDuino

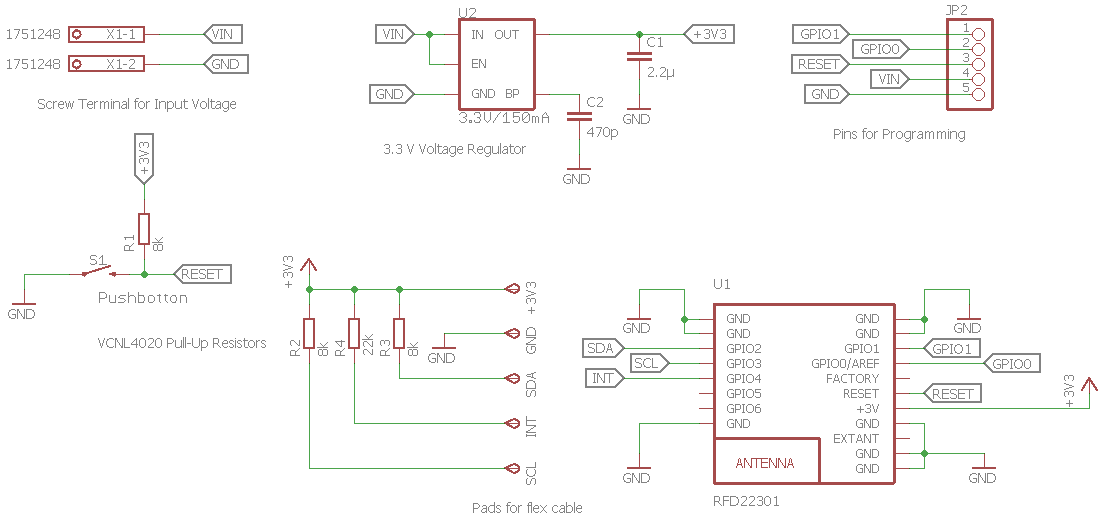
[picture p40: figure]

## Blurry screen

- First trial: platform independent (Java, Python)
- Second trial: only Mac OS X (Objective-C)
- Uses CoreGraphics framework
- Menubar application
- Platform independent application will control the blurring
- Version for Linux and/or Windows if we have time

## Blurry screen

Wearable Computing Systems

DEMO

## Project plan

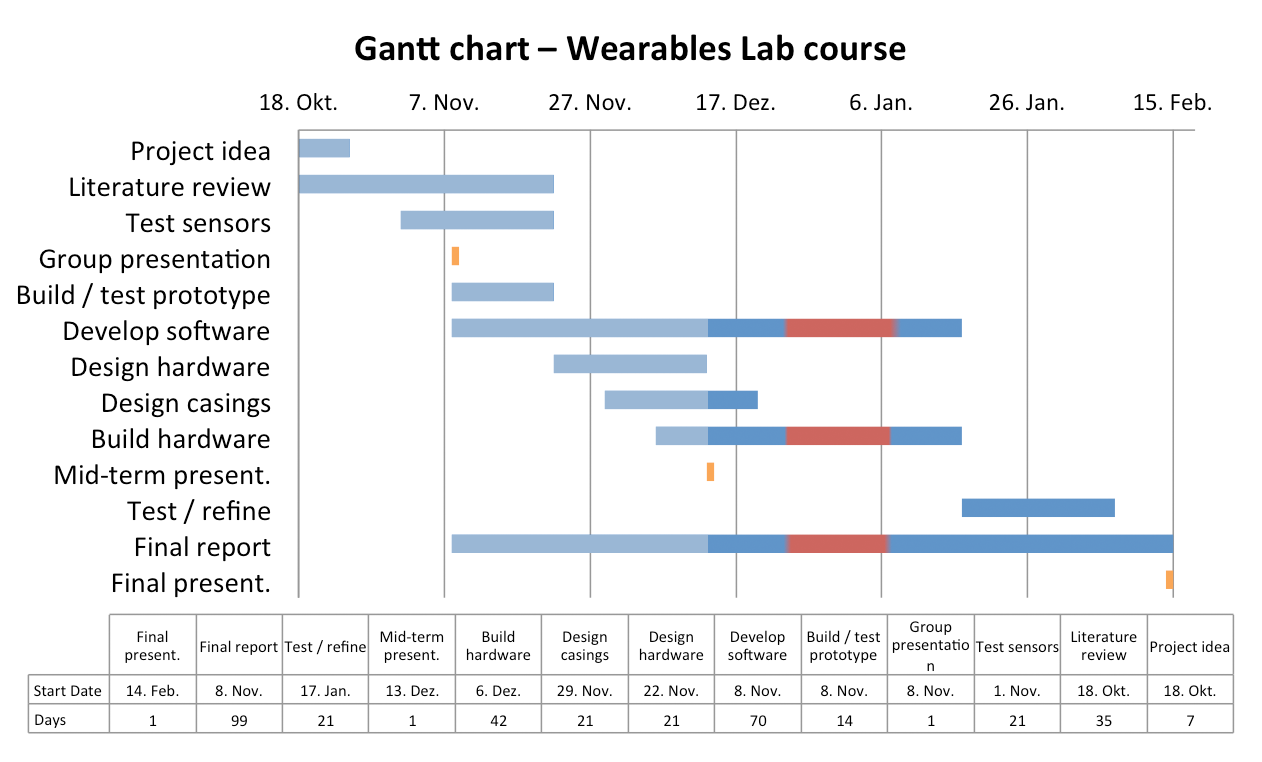
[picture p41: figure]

## Eye blink detection

DEMO

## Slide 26

Thank you for your attention!

## Ball Joint

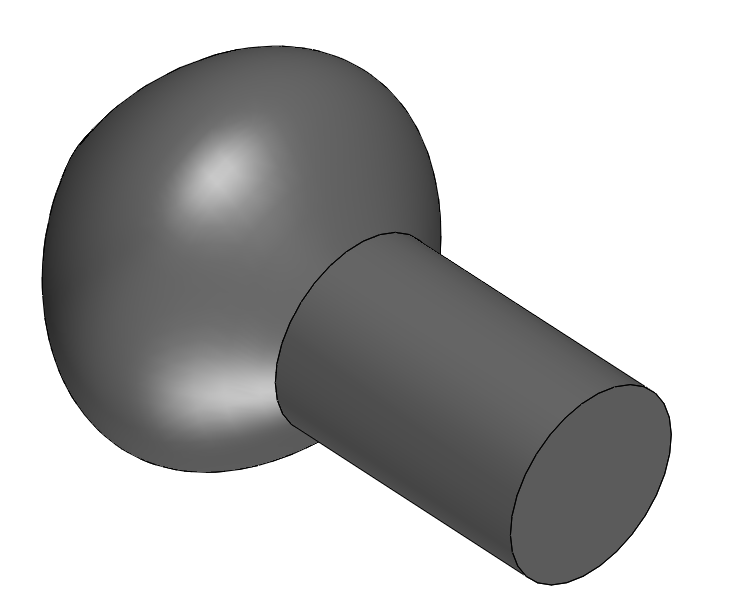
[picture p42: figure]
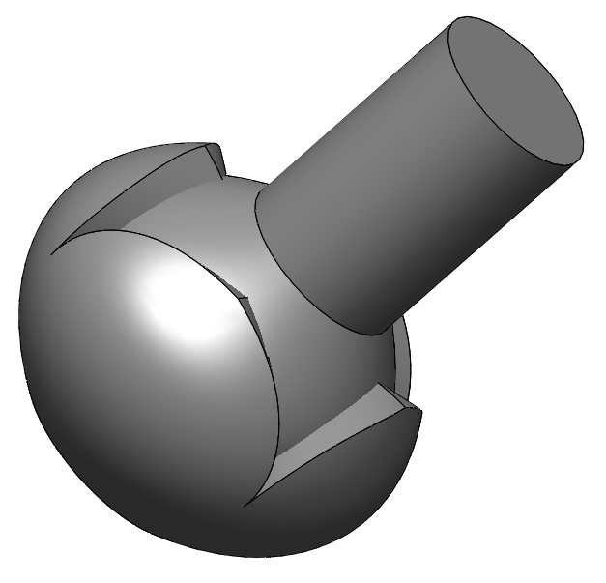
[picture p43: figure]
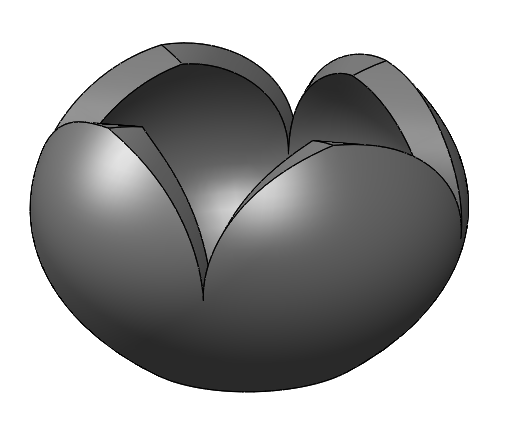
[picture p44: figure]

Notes: Gyroscope, accelerometer, geomagnetic sensor
I²C, UART

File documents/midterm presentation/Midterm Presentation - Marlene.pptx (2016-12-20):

## Wearable Computing Systems eyeDrops

Lab Course 2016 / 2017
Marlene Fiedler
Lorenz Miething
Benjamin Thiemann

Albert-Ludwigs-Universität Freiburg

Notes: Begrüßung

Name

Thema

## Contents

- Blink detection – proof of concept
- Components
- Clip design
- Platine
- Blurry screen
- Project plan
- Summary

eyeDrops

## Blink detection

- Lorenz

## Components

- RFDuino
  - Arduino compatible microcontroller
  - Bluetooth low energy RF module


http://www.rfduino.com/wp-content/uploads/2014/03/RFD22301.Prospective.Top_.png

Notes: Arduino compatible Microcontroller
With a bluetooth low energy RF module
We use SMD version
ADC
Interfaces: I²C, UART, SPI, GPIO
Wireless communication with iOS and android smartphones

## Components

- RFDuino
  - Arduino compatible microcontroller
  - Bluetooth low energy RF module
- VCNL4020
  - Ambient light sensor
  - Proximity sensor
  - Interrupt function


http://www.vishay.com/docs/83476/vcnl4020.pdf

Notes: I²C
Ambient light not used right now, maybe later

## Components

- RFDuino
  - Arduino compatible microcontroller
  - Bluetooth low energy RF module
- VCNL4020
  - Ambient light sensor
  - Proximity sensor
  - Interrupt function
- BNO055
  - Absolute orientation sensor


http://www.mouser.com/images/microsites/Bosch_BNO055.jpg

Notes: optional
Gyroscope, accelerometer, geomagnetic sensor
I²C, UART

## Assembly on glasses


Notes: Gyroscope, accelerometer, geomagnetic sensor
I²C, UART

## Assembly on glasses


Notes: Gyroscope, accelerometer, geomagnetic sensor
I²C, UART

## Assembly on glasses


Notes: Gyroscope, accelerometer, geomagnetic sensor
I²C, UART

## Clip

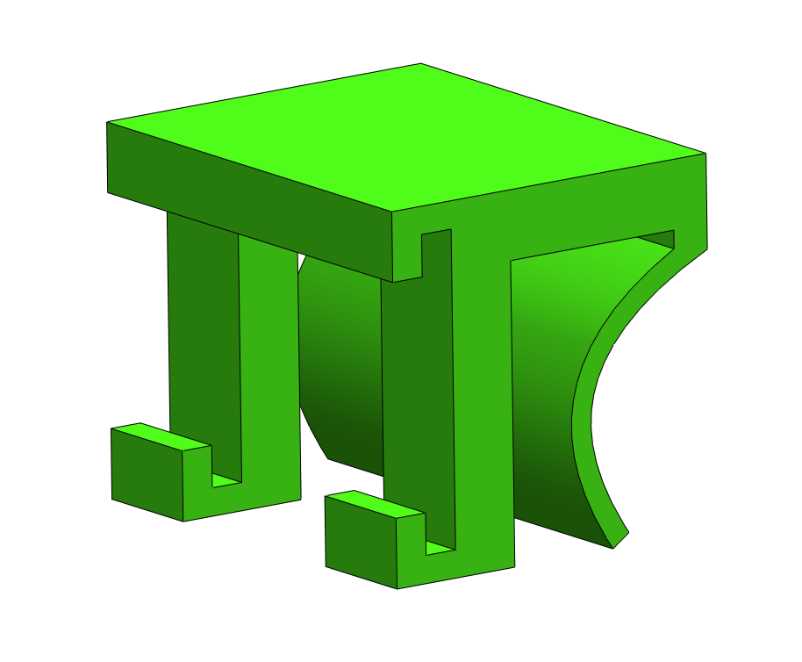
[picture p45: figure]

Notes: Gyroscope, accelerometer, geomagnetic sensor
I²C, UART

## Clip


www.anz-verlag.de

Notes: Gyroscope, accelerometer, geomagnetic sensor
I²C, UART

## Ball Joint


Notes: Gyroscope, accelerometer, geomagnetic sensor
I²C, UART

## Blurry screen

- First trial: platform independent (Java, Python)
- Second trial: only Mac OS X (Objective-C)
- Now working …. see Demo:

## PCB for VCNL4020


## PCB for VCNL4020


## PCB for VCNL4020 – smaller


## PCB for VCNL4020 – smaller


## PCB for VCNL4020


## PCB for VCNL4020


## Project plan


## Summary

- Wearable blink detection system
- Unconscious blink triggering
- Long term protection against dry eyes
- Use blink as input for various applications

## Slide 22

Thank you for your attention!

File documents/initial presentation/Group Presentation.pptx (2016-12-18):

## Wearable Computing Systems eyeDrops

Lab Course 2016 / 2017
Marlene Fiedler
Lorenz Miething
Benjamin Thiemann

Albert-Ludwigs-Universität Freiburg

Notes: Begrüßung

Name

Thema

## Contents

- Motivation
- Project Idea
- Plan A
- Plan B
- Plan C
- Other possible applications
- Project plan
- Summary

Wearable Computing Systems

## Motivation

- Dry eyes due to looking at computer monitor
→ increased probability of eye infections
→ damage of the corneal surface
→ itchy eyes


https://hylo.de/wp-content/uploads/2015/11/pc-arbeit-trockene-augen.jpg

## Idea

- Sensor that detects blinking
  - Proximity Sensor
  - Light Sensor
  - Motion Sensor


http://www.vishay.com/docs/83476/vcnl4020.pdf

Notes: http://www.vishay.com/docs/83476/vcnl4020.pdf

## Idea

- Sensor that detects blinking
  - Proximity Sensor
  - Light Sensor
  - Motion Sensor
- Attached to eye glasses


https://www.blogcdn.com/www.engadget.com/media/2013/05/glasslead.jpg

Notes: Explain that we want to attach the sensor to the wearers own glasses!

## Idea

- Sensor that detects blinking
  - Proximity Sensor
  - Light Sensor
  - Motion Sensor
- Attached to eye glasses
- Blurring of monitor to trigger blinking


http://www.chip.de/ii/770454642_c0a8e0f884.jpg

## Plan A - best case scenario

- Build reliable blink detection system
  - Distance or ambient light sensor
  - Proof of concept
  - Bluetooth communication
  - 3D-printed casing
  - Software for all operating systems to blurr full screen
  - Power with solar cell
- Survey to test system performance
- Develop additional applications with „blink“ as input

## Plan B – alternative scenario

- Use Google Glass instead of self built blink detector
  - Software for all operating systems to blurr screen
  - Focus on software and additional applications


http://betanews.com/wp-content/uploads/2015/01/google_glass-800x450.jpg

Communication between Google Glass and PC
Blurr the screen
Additional applications
Survey to test system performance

## Plan C – worst case scenario

- Use Google Glass instead of self built blink detector
  - Simplified software for one OS


http://betanews.com/wp-content/uploads/2015/01/google_glass-800x450.jpg

## Other possible applications

- Prevention of microsleep when driving
→ acoustic signal
- Simple games
- Input device for disabled people


http://partner.a-z.ch/partnersite/schweiz/jeder-fuenfte-verkehrsunfall-wegen-sekundenschlaf-100812548

## Project plan


## Task distribution

- Hardware design and building (Marlene, Lorenz)
- Case design (Marlene)
- Software design and development (Everybody)
  - RFDuino (Lorenz)
  - PC (Benjamin)
- Project management (Benjamin)
- Survey (Marlene, Benjamin)

## Summary

- Wearable blink detection system
- Unconscious blink triggering
- Long term protection against dry eyes
- Use blink as input for various applications

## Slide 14

Thank you for your attention!

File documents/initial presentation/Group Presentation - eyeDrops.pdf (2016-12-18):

## Wearable Computing Systems eyeDrops

Lab Course 2016 / 2017

Marlene Fiedler
Lorenz Miething
Benjamin Thiemann

Albert-Ludwigs-Universität Freiburg

## Contents

n | Motivation
n | Project Idea
n | Plan A
n | Plan B
n | Plan C
n | Other possible applications
n | Project plan
n | Summary
Wearable Computing Systems | 1

## Motivation

n | Dry eyes due to looking at computer monitor
| à increased probability of eye infections à damage of the corneal surface à itchy eyes


https://hylo.de/wp-content/uploads/2015/11/pc-arbeit-trockene-augen.jpg

## Idea

n | Sensor that detects blinking
n | Proximity Sensor
n | Light Sensor
n | Motion Sensor


http://www.vishay.com/docs/83476/vcnl4020.pdf

## Idea

n | Sensor that detects blinking
n | Proximity Sensor
n | Light Sensor
n | Motion Sensor
n | Attached to eye glasses


https://www.blogcdn.com/www.engadget.com/media/2013/05/glasslead.jpg

## Idea

n | Sensor that detects blinking
n | Proximity Sensor
n | Light Sensor
n | Motion Sensor
n | Attached to eye glasses


n | Blurring of monitor to trigger blinking http://www.chip.de/ii/
770454642_c0a8e0f884.
jpg

## Plan A - best case scenario

n | Build reliable blink detection system
n | Distance or ambient light sensor
n | Proof of concept
n | Bluetooth communication
n | 3D-printed casing
n | Software for all operating systems to blurr full screen
n | Power with solar cell
n | Survey to test system performance
n | Develop additional applications with „blink“ as input

## Plan B – alternative scenario

n | Use Google Glass instead of self built blink detector
n | Software for all operating systems to blurr screen
n | Focus on software and additional applications


http://betanews.com/wp-content/uploads/2015/01/google_glass-800x450.jpg

n | Communication between Google Glass and PC
n | Blurr the screen
n | Additional applications
n | Survey to test system performance

## Plan C – worst case scenario

n | Use Google Glass instead of self built blink detector
n | Simplified software for one OS

http://betanews.com/wp-content/uploads/2015/01/google_glass-800x450.jpg


## Other possible applications

n | Prevention of microsleep when driving
| à acoustic signal
n | Simple games
n | Input device for disabled people


http://partner.a-z.ch/partnersite/schweiz/jeder-fuenfte-verkehrsunfall-wegen-sekundenschlaf-100812548

## Project plan


## Task distribution

n | Hardware design and building (Marlene, Lorenz)
n | Case design (Marlene)
n | Software design and development (Everybody)
n | RFDuino (Lorenz)
n | PC (Benjamin)
n | Project management (Benjamin)
n | Survey (Marlene, Benjamin)

## Summary

n | Wearable blink detection system
n | Unconscious blink triggering
n | Long term protection against dry eyes
n | Use blink as input for various applications

## Thank you for your attention!

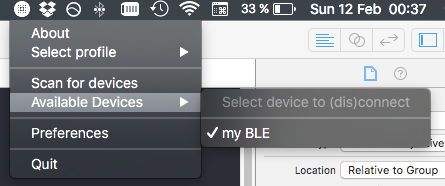
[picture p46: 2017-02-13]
docs/img/menu_devices.png

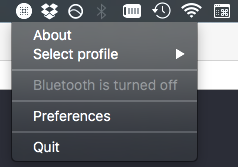
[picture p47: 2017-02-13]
docs/img/menu_ble_turned_off.png

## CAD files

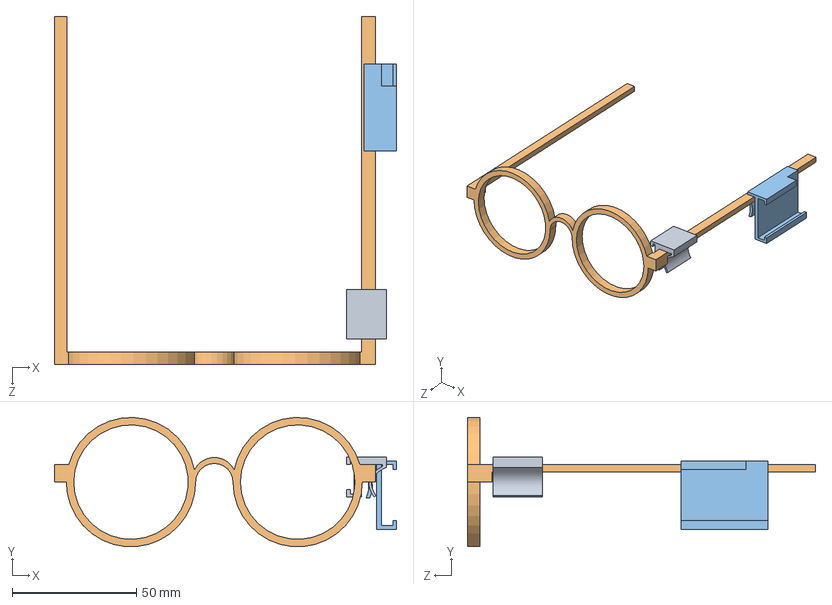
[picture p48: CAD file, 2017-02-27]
hardware/3dprinting/solidworks/Glasses-with-clips-for-poster.SLDASM
137.5 x 51.9 x 140.0 mm
Clip-4
Brille
Clip-RFDuino-Board-7

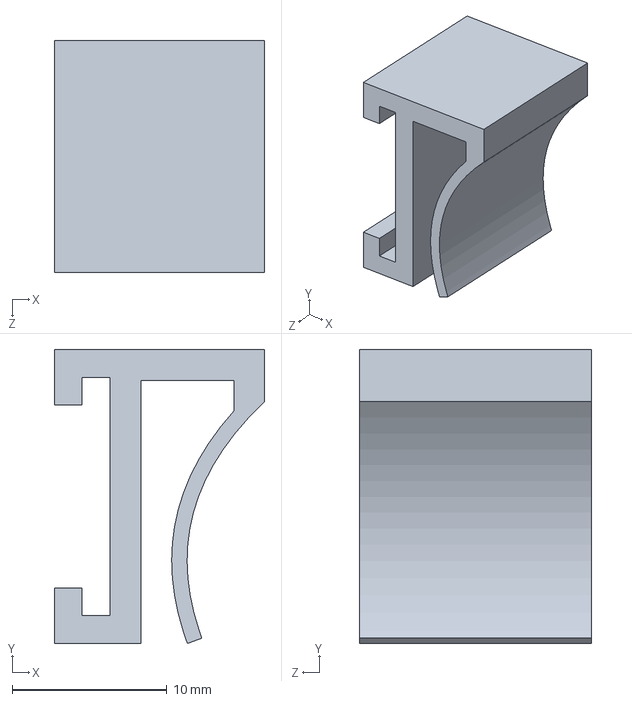
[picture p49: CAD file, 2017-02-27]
hardware/3dprinting/solidworks/Clip-7-narrow-2.SLDPRT
13.6 x 19.0 x 15.0 mm

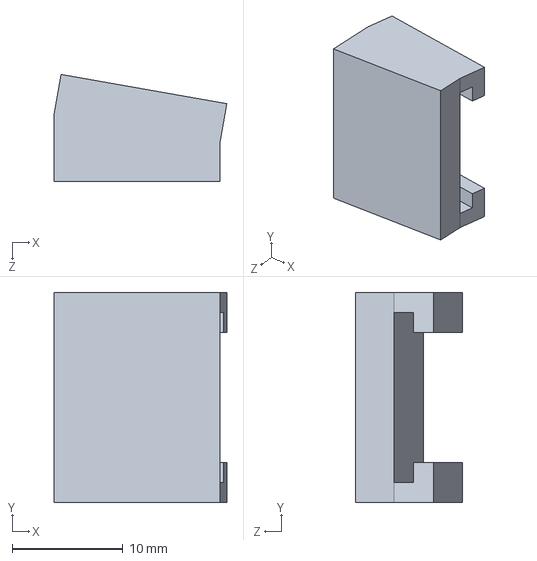
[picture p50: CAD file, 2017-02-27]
hardware/3dprinting/solidworks/Magnetic-Adapter-10-degrees.SLDPRT
15.6 x 19.0 x 9.69 mm

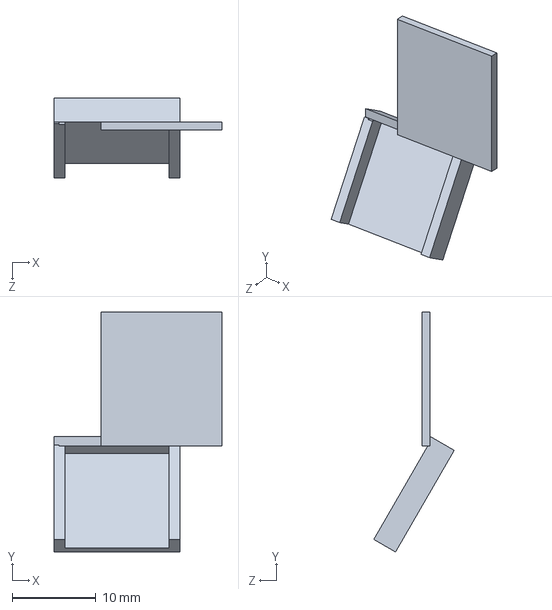
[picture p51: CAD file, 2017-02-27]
hardware/3dprinting/solidworks/Slider-3-lower.SLDPRT
20.0 x 28.6 x 9.60 mm

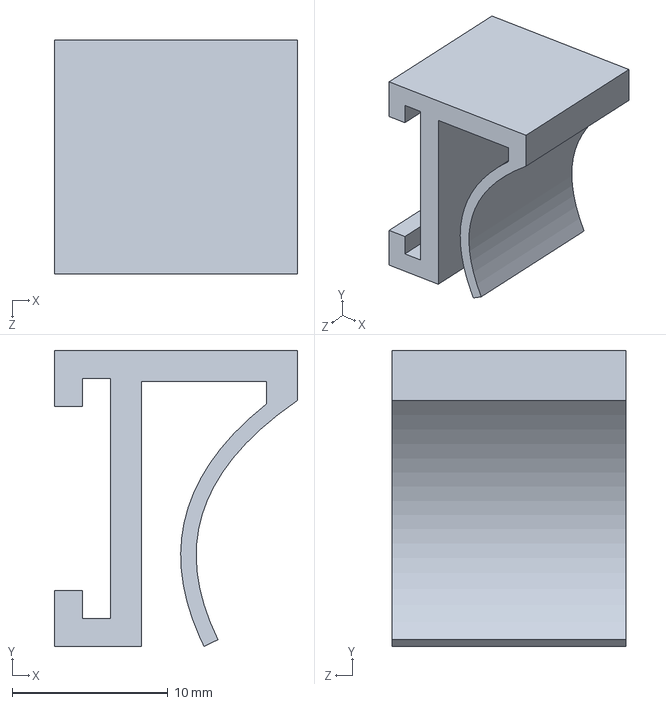
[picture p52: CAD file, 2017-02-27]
hardware/3dprinting/solidworks/Clip-7-narrow.SLDPRT
15.6 x 19.0 x 15.0 mm

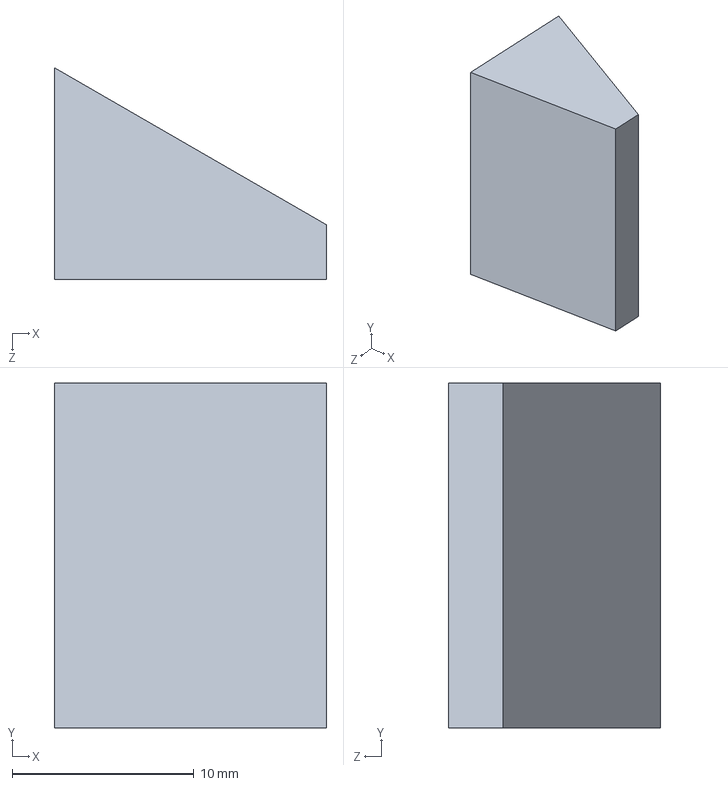
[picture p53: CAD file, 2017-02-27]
hardware/3dprinting/solidworks/Magnetic-Adapter-30-degrees.SLDPRT
15.0 x 19.0 x 11.7 mm

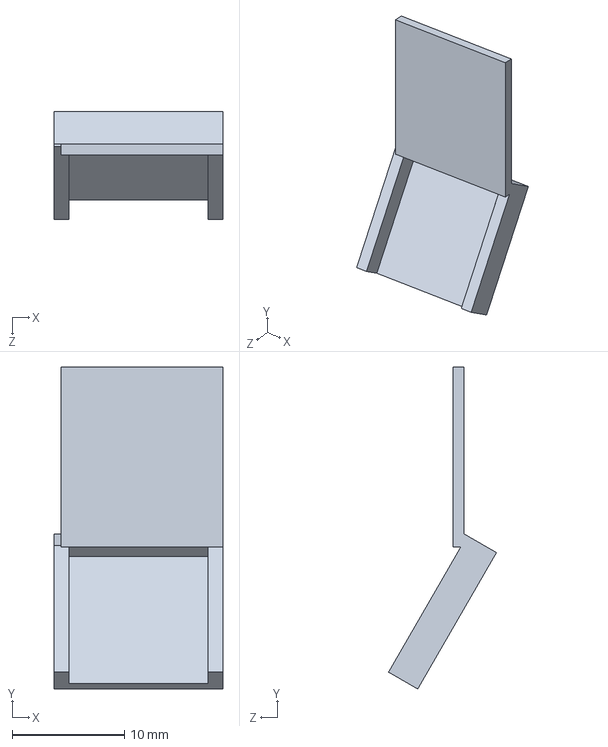
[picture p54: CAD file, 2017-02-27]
hardware/3dprinting/solidworks/Slider-3.SLDPRT
15.0 x 28.6 x 9.60 mm

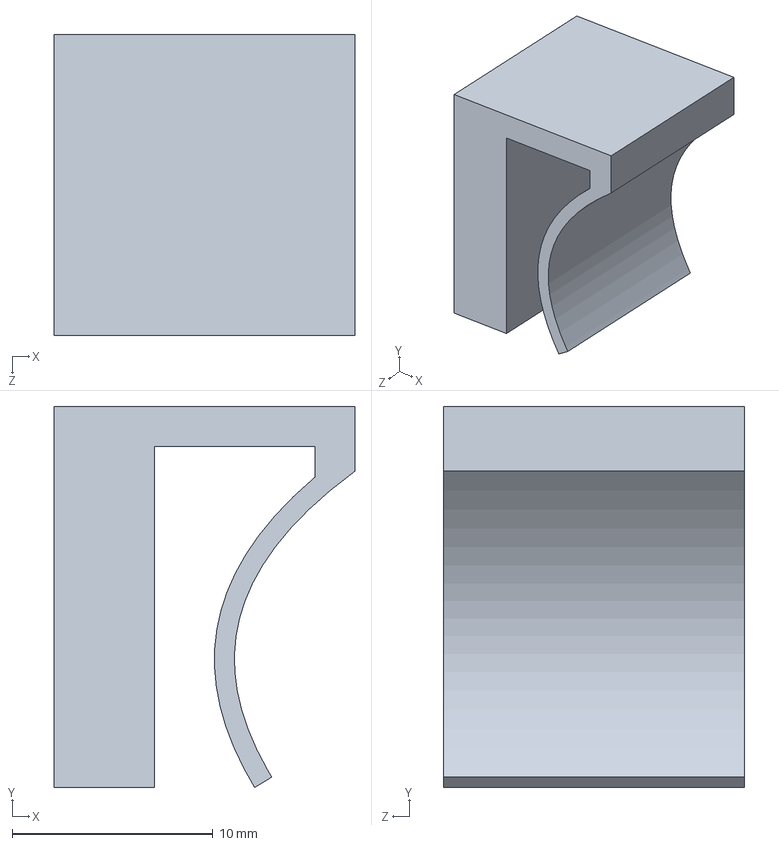
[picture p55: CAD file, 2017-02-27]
hardware/3dprinting/solidworks/Clip-with-magnets-7.SLDPRT
15.0 x 19.0 x 15.0 mm

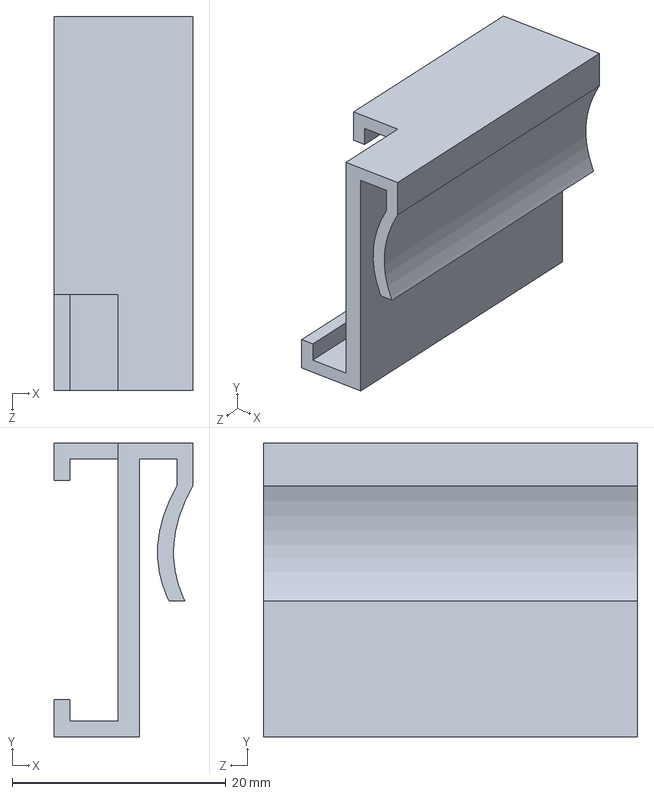
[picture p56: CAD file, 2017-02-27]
hardware/3dprinting/solidworks/Clip-RFDuino-Board-7.SLDPRT
13.0 x 27.5 x 35.0 mm

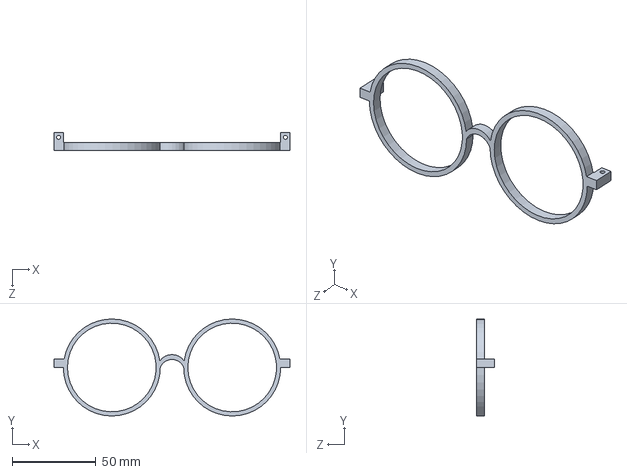
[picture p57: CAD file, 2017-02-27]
hardware/3dprinting/solidworks/Brille-ohne-Buegel-5.SLDPRT
141.1 x 58.0 x 11.0 mm

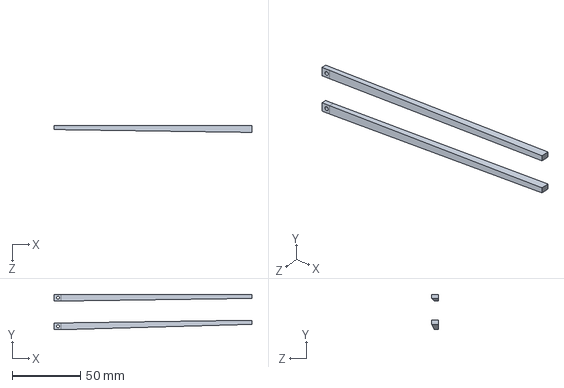
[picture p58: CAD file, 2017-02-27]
hardware/3dprinting/solidworks/Brillenbuegel--2.SLDPRT
145.0 x 25.9 x 5.00 mm

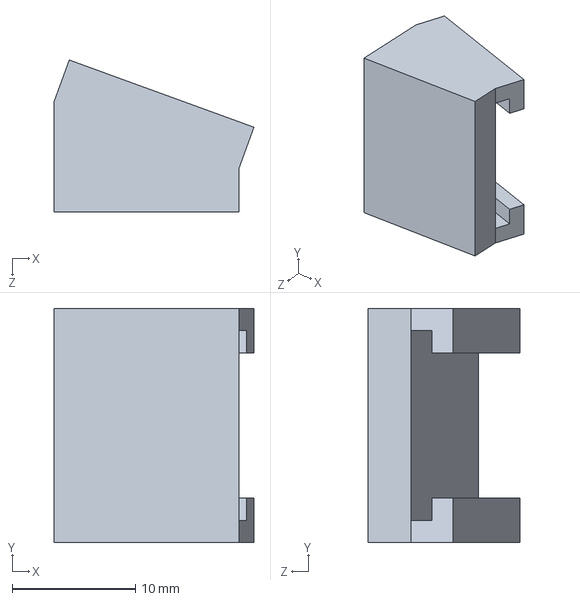
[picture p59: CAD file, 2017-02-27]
hardware/3dprinting/solidworks/Magnetic-Adapter-20-degrees.SLDPRT
16.2 x 19.0 x 12.3 mm

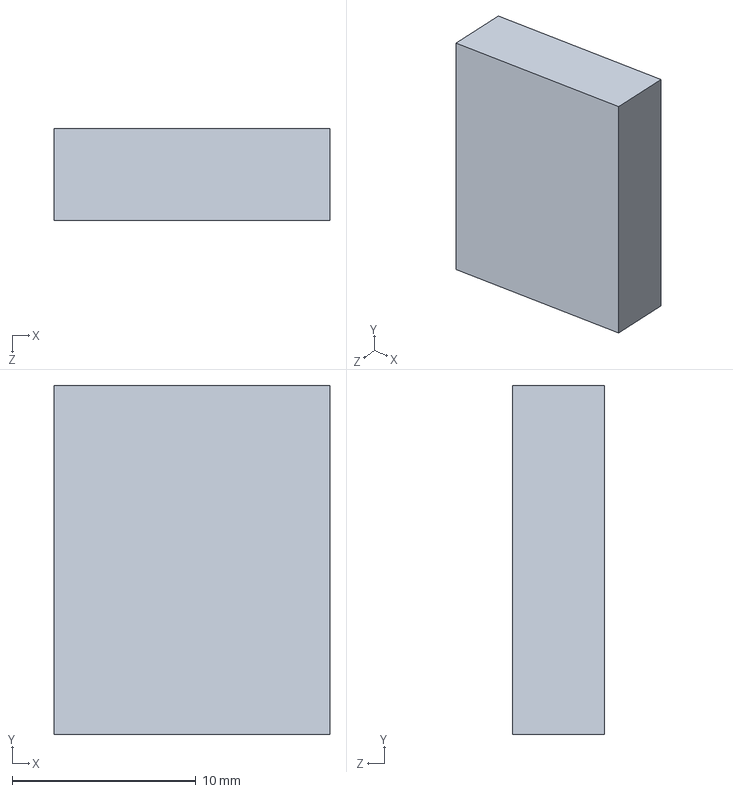
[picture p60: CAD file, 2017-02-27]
hardware/3dprinting/solidworks/Magnetic-Adapter.SLDPRT
15.0 x 19.0 x 5.00 mm

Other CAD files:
hardware/3dprinting/solidworks/Clip-7-wider.SLDPRT
hardware/3dprinting/solidworks/Brille-ohne-Buegel-5.STL
hardware/3dprinting/solidworks/Brillenbuegel-2.STL
hardware/3dprinting/solidworks/Clip-7-narrow-2.STL
hardware/3dprinting/solidworks/Clip-7-narrow.STL
hardware/3dprinting/solidworks/Clip-7-wider.STL
hardware/3dprinting/solidworks/Clip-RFDuino-Board-7.STL
hardware/3dprinting/solidworks/Clip-with-magnets-7.STL
hardware/3dprinting/solidworks/Magnetic-Adapter-10-degrees.STL
hardware/3dprinting/solidworks/Magnetic-Adapter-20-degrees.STL
hardware/3dprinting/solidworks/Magnetic-Adapter-30-degrees.STL
hardware/3dprinting/solidworks/Slider-3-lower.STL
hardware/3dprinting/solidworks/Slider-3.STL

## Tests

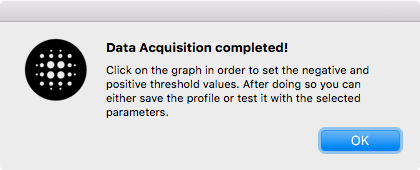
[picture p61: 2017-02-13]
docs/img/calibration_complete.png

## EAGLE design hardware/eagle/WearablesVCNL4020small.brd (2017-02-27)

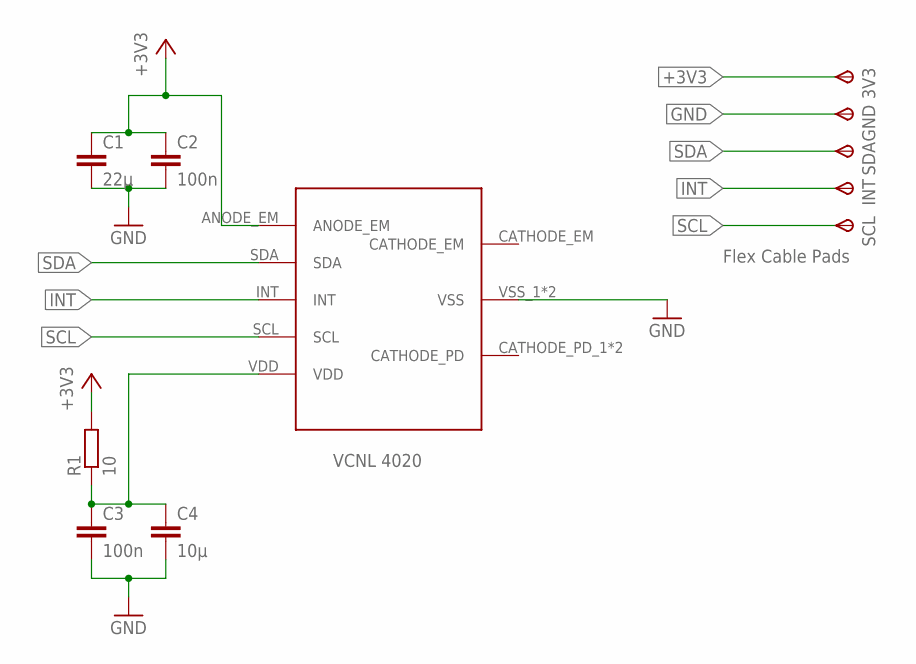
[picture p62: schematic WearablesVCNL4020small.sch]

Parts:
3V3: TPSTP08R; TP08R
C1: 22µ; C0603
C2, C3: 100n; C0603
C4: 10µ; C0603
GND: TPSTP08R; TP08R
INT: TPSTP08R; TP08R
R1: 10; R0603
SCL: TPSTP08R; TP08R
SDA: TPSTP08R; TP08R
U$1: VCNL4020

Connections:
+3V3: 3V3.TP, C1.1, C2.1, R1.2, U$1.ANODE_EM
GND: C1.2, C2.2, C3.2, C4.2, GND.TP, U$1.VSS_1 (VSS), U$1.VSS_2 (VSS)
INT: INT.TP, U$1.INT
SCL: SCL.TP, U$1.SCL
SDA: SDA.TP, U$1.SDA
VDD: C3.1, C4.1, R1.1, U$1.VDD

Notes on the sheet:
VCNL 4020
Flex Cable Pads

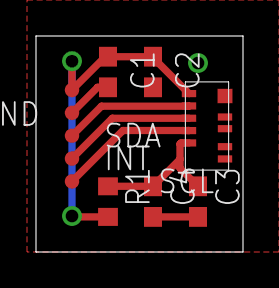
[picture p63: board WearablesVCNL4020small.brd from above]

Board: 2 copper layers, 11.5 x 12.0 mm, 11 parts (0 on the bottom side), 6 nets.

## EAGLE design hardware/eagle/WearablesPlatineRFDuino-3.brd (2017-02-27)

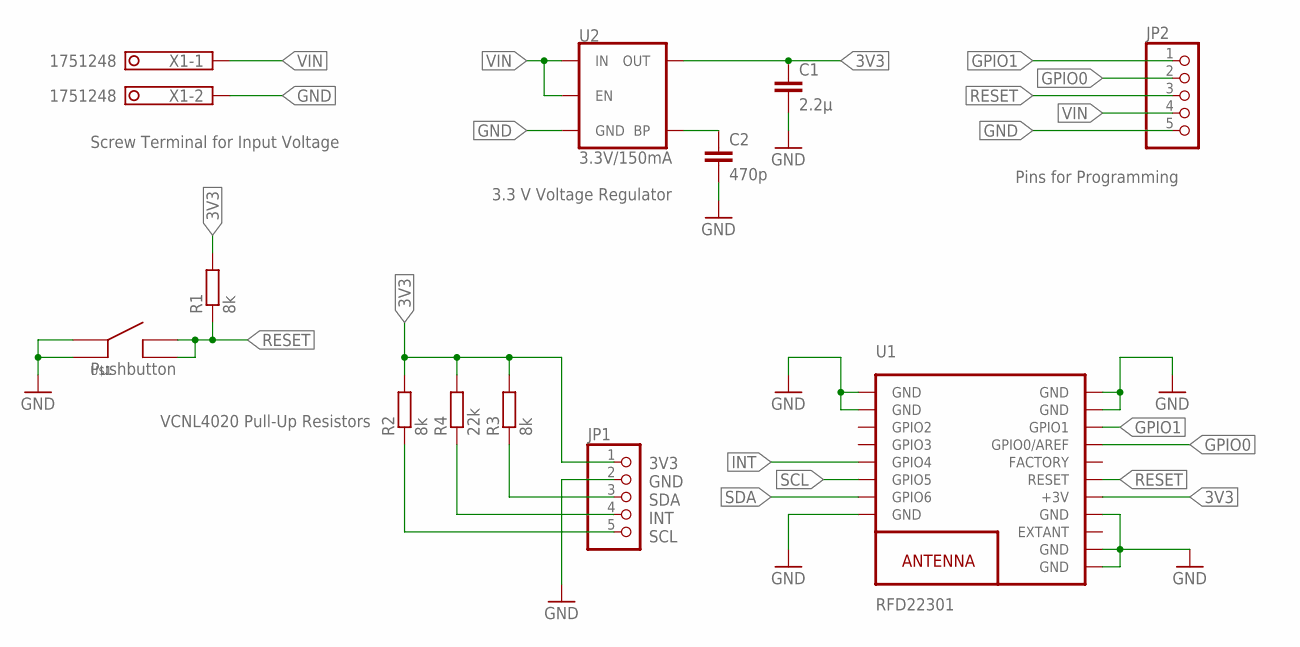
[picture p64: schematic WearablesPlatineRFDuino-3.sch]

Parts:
C1: 2.2µ; C0603
C2: 470p; C0603
JP1, JP2: PINHD-1X5; 1X05
R1, R2, R3: 8k; R0603
R4: 22k; R0603
U1: RFD22301
U2: 3.3V/150mA; SOT23-5
U$1: TACTILE_SWITCH; EVQ-PUK02K
X1: 1751248

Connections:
3V3: C1.1, JP1.1, R1.2, R2.2, R3.2, R4.2, U1.13 (+3V), U2.5 (OUT)
GND: C1.2, C2.2, JP1.2, JP2.5, U1.1 (GND), U1.2 (GND), U1.8 (GND), U1.9 (GND), U1.10 (GND), U1.12 (GND), U1.18 (GND), U1.19 (GND), U2.2 (GND), U$1.1 (A), U$1.3 (A), X1.2
GPIO0: JP2.2, U1.16 (GPIO0/AREF)
GPIO1: JP2.1, U1.17 (GPIO1)
INT: JP1.4, R4.1, U1.5 (GPIO4)
unnamed: C2.1, U2.4 (BP)
RESET: JP2.3, R1.1, U1.14 (RESET), U$1.2 (B), U$1.4 (B)
SCL: JP1.5, R2.1, U1.6 (GPIO5)
SDA: JP1.3, R3.1, U1.7 (GPIO6)
VIN: JP2.4, U2.1 (IN), U2.3 (EN), X1.1

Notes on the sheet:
Screw Terminal for Input Voltage
3V3 GND SDA INT SCL
VCNL4020 Pull-Up Resistors
Pins for Programming
3.3 V Voltage Regulator
Pushbutton

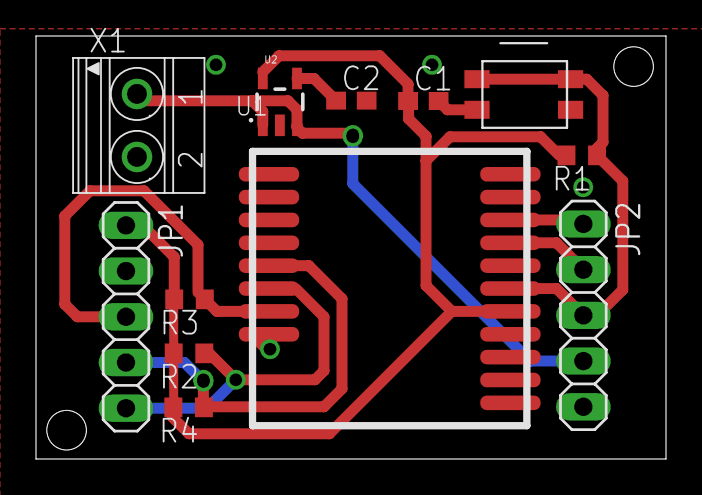
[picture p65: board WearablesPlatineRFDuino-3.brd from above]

Board: 2 copper layers, 35.0 x 23.5 mm, 12 parts (0 on the bottom side), 10 nets.

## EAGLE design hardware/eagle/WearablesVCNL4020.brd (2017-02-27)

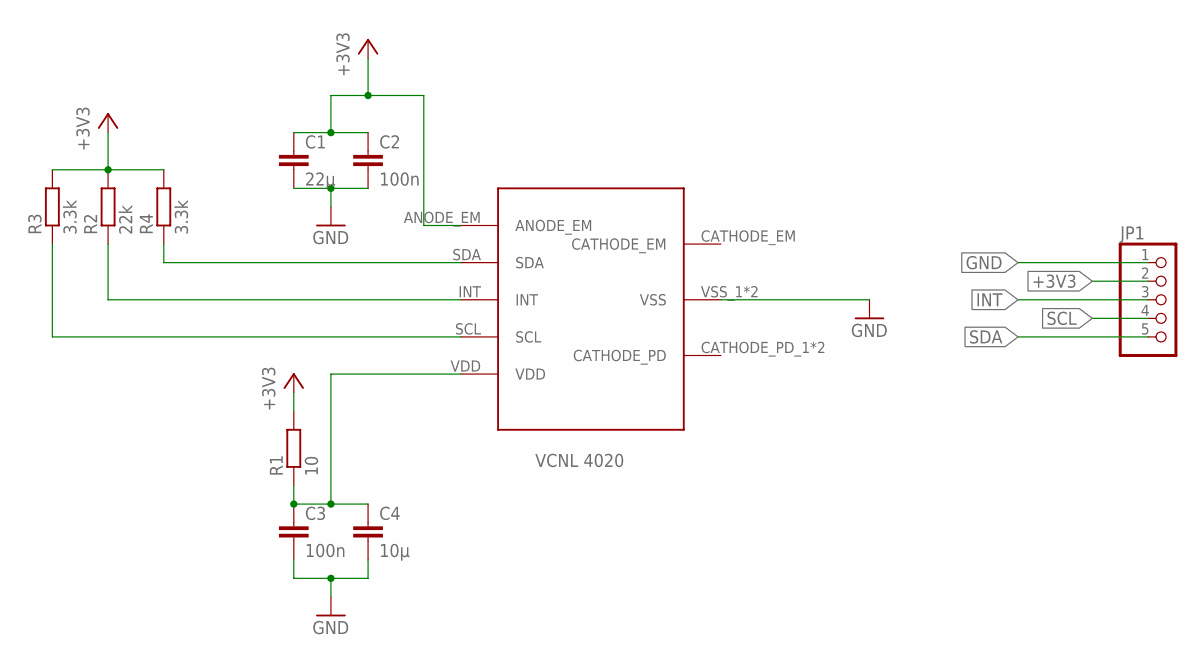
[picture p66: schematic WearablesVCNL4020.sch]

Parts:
C1: 22µ; C0805
C2, C3: 100n; C0805
C4: 10µ; C0805
JP1: PINHD-1X5/90; 1X05/90
R1: 10; R0805
R2: 22k; R0805
R3, R4: 3.3k; R0805
U$1: VCNL4020

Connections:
+3V3: C1.1, C2.1, JP1.2, R1.2, R2.2, R3.2, R4.2, U$1.ANODE_EM
GND: C1.2, C2.2, C3.2, C4.2, JP1.1, U$1.VSS_1 (VSS), U$1.VSS_2 (VSS)
INT: JP1.3, R2.1, U$1.INT
SCL: JP1.4, R3.1, U$1.SCL
SDA: JP1.5, R4.1, U$1.SDA
VDD: C3.1, C4.1, R1.1, U$1.VDD

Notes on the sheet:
VCNL 4020

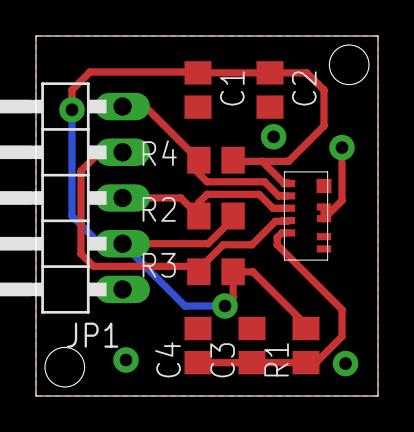
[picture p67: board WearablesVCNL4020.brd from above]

Board: 2 copper layers, 19.0 x 20.0 mm, 10 parts (0 on the bottom side), 6 nets.

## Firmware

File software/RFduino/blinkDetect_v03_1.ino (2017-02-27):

/**
 * MIT License
 *
 * Copyright (c) 2017 University of Freiburg im Breisgau, Germany,
 * Marlene Fiedler <fiedlerm@informatik.uni-freiburg.de>,
 * Lorenz Miething <miethinl@informatik.uni-freiburg.de>,
 * Benjamin Thiemann <benjamin.thiemann@neptun.uni-freiburg.de>
 * 
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
 * THE SOFTWARE IS PROVIDED "AS IS", WITHOUT WARRANTY OF ANY KIND, EXPRESS OR
 * IMPLIED, INCLUDING BUT NOT LIMITED TO THE WARRANTIES OF MERCHANTABILITY,
 * FITNESS FOR A PARTICULAR PURPOSE AND NONINFRINGEMENT. IN NO EVENT SHALL THE
 * AUTHORS OR COPYRIGHT HOLDERS BE LIABLE FOR ANY CLAIM, DAMAGES OR OTHER
 * LIABILITY, WHETHER IN AN ACTION OF CONTRACT, TORT OR OTHERWISE, ARISING FROM,
 * OUT OF OR IN CONNECTION WITH THE SOFTWARE OR THE USE OR OTHER DEALINGS IN THE
 * SOFTWARE.
 */

/**
 *  Pin layout:
 *    SDA GPIO 6
 *    SCL GPIO 5
 *    INT
 */

#include <Arduino.h>
#include <Wire.h>
#include <math.h>
#include "RFduinoBLE.h"


#define VCNL_ADDRESS 0x13 // I2C Address of the VCNL 4020 Sensor
#define CYCLES 200        // Buffersize for the samples and preprocessing.
#define CYCLE_TIME 5      // (in ms) time step, in which samples are obtained processed.

// Comment to deactivate Serial communication.
#define SERIAL_DEBUG

double proximity = 0;             // current proximity value
double lastProximity = 0;         // last proximity value
double ambient = 0.0;             // ambient light measurement - not used
boolean new_data = false;         // flag set true if new data obtained.
boolean mode_calibration = false; // flag if calibration data should be sent.
boolean mode_debug = false;       // flag if debugging data should be sent.
boolean ble_connected = false;    // flag to indicate that RFduino is connected via BLE.

// Blink Profile paramters (can be set via computer app)
float edgePosThresh = 0.0025;     // pos threshold for blink detection
float edgeNegThresh = -0.0035;    // neg threshold for blink detection
float hyst = 0.0002;              // not applied to zero crossing intentionally (doesn't cross all the way all the time).
float max_max = 0.02;             // everything bigger than this as maximum is ignored
float min_min = -0.02;            // everything smaller than this as minimum is ignored.
uint8_t* t_fall;                  // two values indicating min and max samples allowed for falling edge
uint8_t* t_rise;                  // two values indicating min and max samples allowed for rising edge
uint16_t* t_total;                // two values indicating min and max samples allowed for total blink duration
uint8_t allowedZeros = 4;         // allowed sample number the eye is closed during an eye blink

// Internal data structure variables
float* proxFilteredBuffer;        // CYCLES is size of buffer. Proximity value samples from that buffer are analyzed to find blinks
uint8_t iP = 0;                   // index for proxFilteredBuffer used in circular array fashion.
float proxFiltered = 0.0;         // current filtered value (with moving average filter)

// other variables
int blinkAckAmount = 10;           // send blink message multiple times to accomodate package loss.
int blinkAckCounter = 0;           // counter used to keep track how often it was sent.
unsigned long updateTime = 0;     // Last time the a value was received from the sensor.

/**
 * Arduino default setup function.
 */
void setup() {
  // not used here...// Activate pulldown for unused pins to avoid leakage currents for floating pins.
  Wire.begin(); // start I2C interface
#ifdef SERIAL_DEBUG
  override_uart_limit = true; // allow fast serial communiation while using BLE.
  Serial.begin(115200);
#endif
  init_device();
}

/**
 * Arduino default Loop function
 */
void loop() {
  if (updateVCNL4020()) {
    boolean justBlinked = detectBlinks();
    updateBLE(justBlinked | blinkAckCounter);
    if (justBlinked) {
#ifdef SERIAL_DEBUG
      Serial.println("Blinked");
#endif
      blinkAckCounter = blinkAckAmount;
    }
    if (blinkAckCounter > 0) {
      --blinkAckCounter;
    }
    // send RFduino in power saving mode until cycle time is met.
    // Seems to fuck up calibration mode some times.
    if (!RFduinoBLE.radioActive && !mode_calibration && !mode_debug) {
      // Deactivated for now. Breakes the bluetooth comunication.
      //RFduino_ULPDelay(CYCLE_TIME - (millis() - updateTime));
    }
  }
}

/**
 * Initializes the device:
 *  - Battery voltage monitoring
 *  - VCNL 4020 proximity and ambient light sensor (multiple times if needed)
 *  - Blink detection algorithm
 *  - Bluetooth Low energy communication
 */
void init_device() {  // TODO remove bugs
#ifdef SERIAL_DEBUG
  Serial.println("\nINITIALIZE DEVICE:");
#endif
  // Set initial mode.
  mode_calibration = false;
  mode_debug = false;
  ble_connected = false;

  // Initialize battery voltage monitoring.
  initBatteryVoltageMonitor();

#ifdef SERIAL_DEBUG
  Serial.print("\tVCNL4020 . . . ");
#endif

  // Init VCNL 4020. In case of failure try 256 times. Finally restart system.
  int i;
  int r = 0;  // result error code
  for (i = 0; i < 256; ++i) {
    r = initVCNL4020();
    if (r == 0)
      break;
    if (i == 255) {
#ifdef SERIAL_DEBUG
      Serial.println("MAJOR ERROR - VCNL4020 Connection issue!");
#endif
      delay(1000);
      RFduino_systemReset(); // restart RFduino and try again.
    }
    delay(20);
  }

#ifdef SERIAL_DEBUG
  Serial.print("Done with code ");
  Serial.print(r);
  Serial.print(" in ");
  Serial.print(i + 1);
  Serial.println(" iterations.");
  Serial.print("\tBlinkdetection . . . ");
#endif

  // Init the blink detection functions such as filters and initial conditions.
  initBlinkdetection();
#ifdef SERIAL_DEBUG
  Serial.println("Done.");
  Serial.print("\tInit BLE . . . ");
#endif

  // Init the bluetooth communication.
  initBLE();
#ifdef SERIAL_DEBUG
  Serial.println("Done.");
  Serial.println("Initialization Successful.");
#endif
}

/**
 * Prerform controlled system reset
 * Terminate any I2C communication
 * Terminate any bluetooth communication
 */
 void resetSystemControlled() {
  // let Wire communication bleed off before resetting device
  if (Wire.available()) {
    while (Wire.available()) {
      Wire.read();
    }
    Wire.endTransmission();
  }

  // terminate bluetooth communication
  RFduinoBLE.end();

  // restart RFduino
  RFduino_systemReset(); 
 }

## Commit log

2016-12-18 Added initial group presentation
    [gantt chart.xlsx]
2016-12-18 Added gantt chart for midterm presentation
    [gantt chart.xlsx]
2017-02-27 added documented Arduino code.

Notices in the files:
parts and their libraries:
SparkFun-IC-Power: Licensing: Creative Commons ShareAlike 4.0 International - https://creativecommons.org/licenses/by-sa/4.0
